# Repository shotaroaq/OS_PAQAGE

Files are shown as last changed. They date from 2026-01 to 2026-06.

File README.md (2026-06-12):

# OS-PAQAGE

"[Open Source microwave Packaging for quantum systems (OS-PAQAGE)](https://doi.org/10.5281/zenodo.18399469)" is a collection of PCB and magnetic-shielded sample-holder designs intended primarily for microwave-frequency use. These designs were developed mainly at RIKEN in Japan and are widely used by Japanese research institutes and universities. Using this package, measurements of superconducting qubits with energy relaxation times exceeding 400 us [1] and observations of internal Q factors above 1e7 in superconducting resonators at the single-photon level have been reported [2].

In fundamental research, there are still many situations where small samples are studied but a clean electromagnetic environment is required. To broaden the available options for building such measurement environments, we decided to release the contents of this repository as open source.

[1] [A. Noguchi, et al. "High-performance transmon qubits with an epitaxially grown TiN film on Si (100) substrate." 2023 APS March Meeting. 2023.](https://meetings.aps.org/Meeting/MAR23/Session/M73.5)
[2] [Y. Tominaga, et al. "Intrinsic quality factors approaching 10 million in superconducting planar resonators enabled by spiral geometry." EPJ Quantum Technology 12.1 (2025): 60.](https://link.springer.com/article/10.1140/epjqt/s40507-025-00367-w)

## Usage
Please place an order for the jigs with a nearby factory. Assembly instructions are provided in *doc/pcb_sample_holder_instructions.pdf*.
In our case, we outsource PCB manufacturing to KANSAI DENSHI INDUSTRIES.

## License
This repository is released under the MIT License. See `LICENSE`.

## Citation
If you use the contents of this repository, please cite the project in the following format:

```
@Misc{osPAQAGE,
  author = {Shirai, Shotaro and Noguchi, Atsushi},
  title = {{OS-PAQAGE}: A open source microwave packaging for quantum systems},
  year = {2025--},
  url = "https://doi.org/10.5281/zenodo.18399470",
  note = {[Online; accessed <today>]}
}
```

## Acknowledgements
This work has been supported by funding from JST Moonshot R&D Program (Grant Number JPMJMS2067)

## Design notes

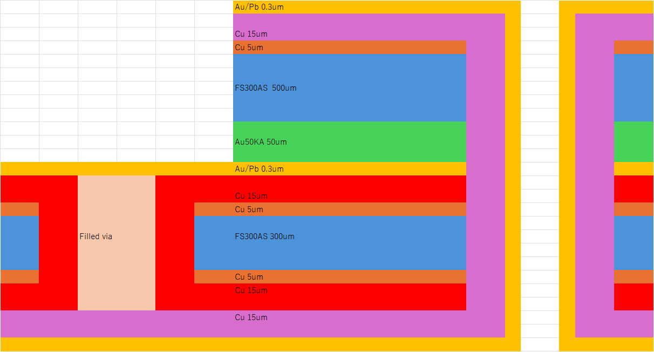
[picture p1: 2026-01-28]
pcb/layer.png

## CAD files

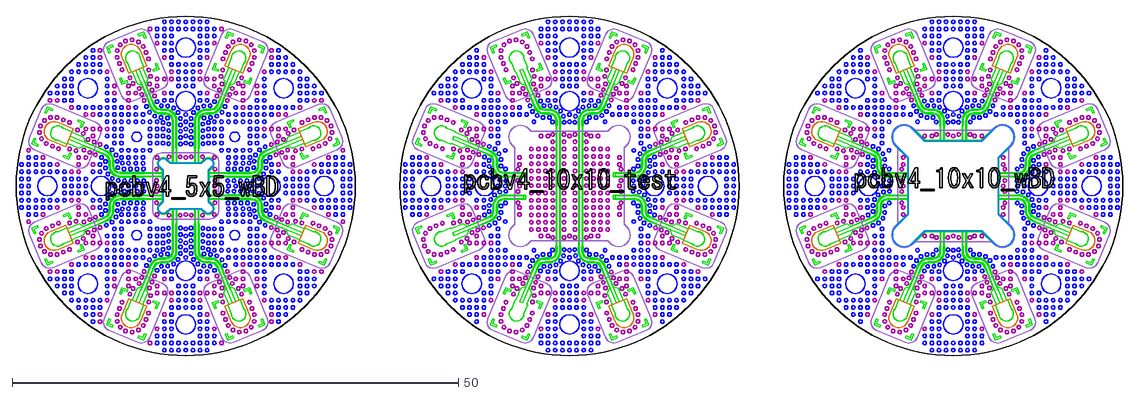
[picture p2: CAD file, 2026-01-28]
pcb/3lay_Cavity_240918.dxf
124.0 x 38.0

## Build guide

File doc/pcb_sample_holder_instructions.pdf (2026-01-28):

# Small scale sample holder and PCB

## RIKEN Center for Quantum Computing Komaba Institute for Science, UTokyo

## Shotaro Shirai, Atsushi Noguchi

Ver0.1 2024/10/09

Ver0.2 2024/10/13

Ver0.3 2024/11/07

Ver0.4 2025/04/08

Ver0.5 2025/06/10

Ver0.6 2026/01/26

# Sample holder design

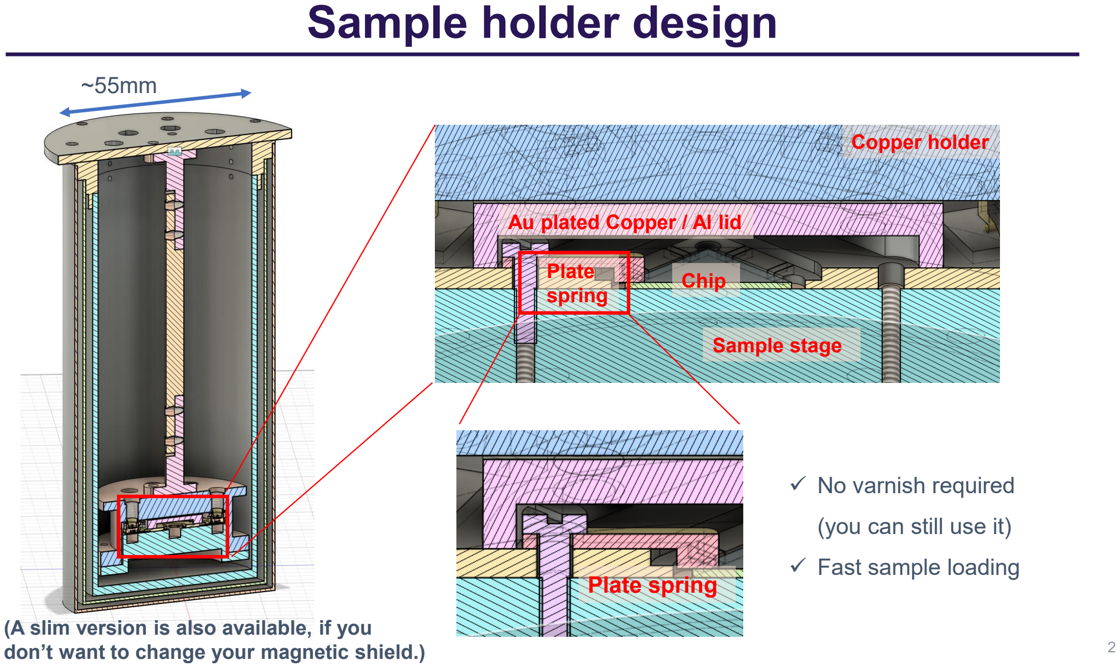
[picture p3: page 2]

~55mm

Au plated Copper / Al lid

Copper holder

Sample stage

Chip Plate
spring

Plate spring

✓ No varnish required

(you can still use it)

✓ Fast sample loading

(A slim version is also available, if you don’t want to change your magnetic shield.)

# PCB design

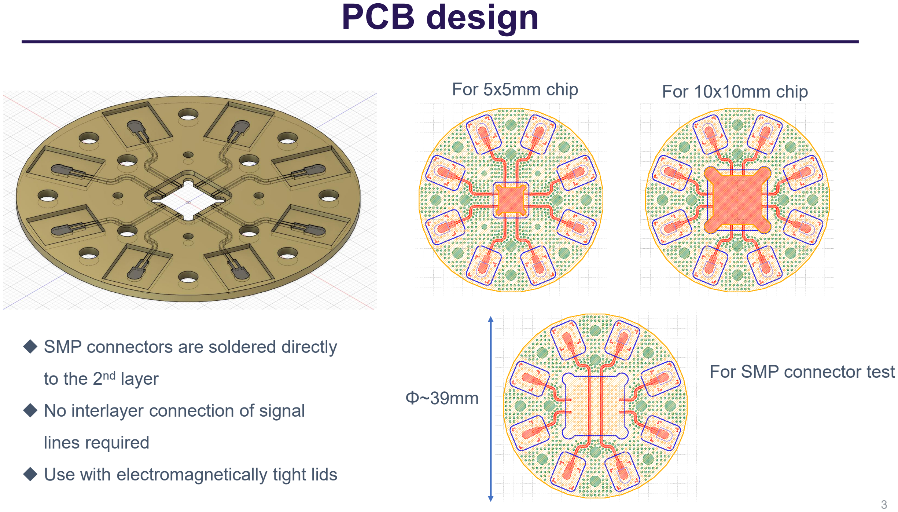
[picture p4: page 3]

For 5x5mm chip | For 10x10mm chip

For SMP connector test

◆ SMP connectors are soldered directly

to the 2nd layer

◆ No interlayer connection of signal

lines required

◆ Use with electromagnetically tight lids

Φ~39mm

# Assembling PCB

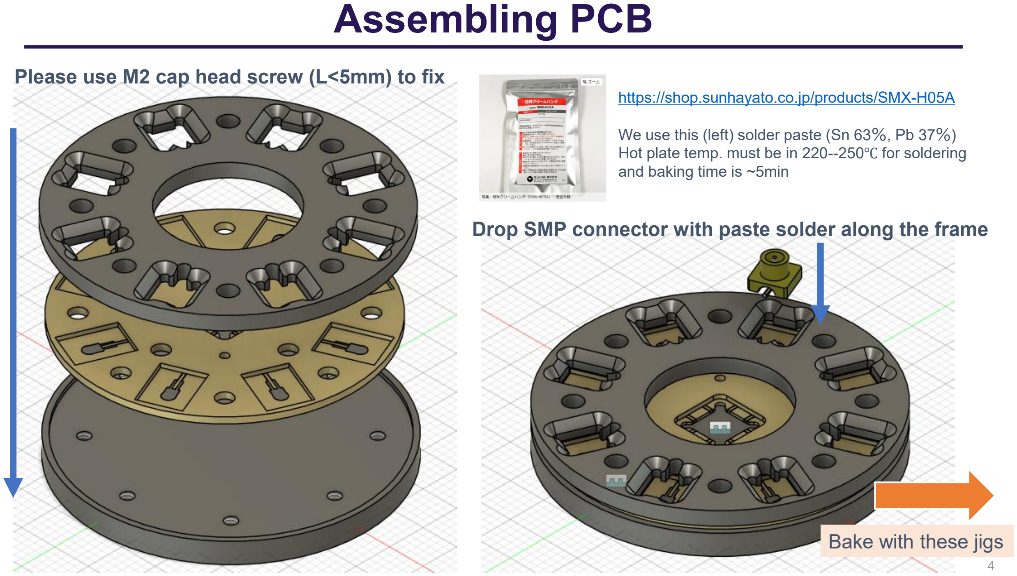
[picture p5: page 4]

Please use M2 cap head screw (L<5mm) to fix

Drop SMP connector with paste solder along the frame https://shop.sunhayato.co.jp/products/SMX-H05A

We use this (left) solder paste (Sn 63％, Pb 37％) Hot plate temp. must be in 220--250℃ for soldering and baking time is ~5min

Bake with these jigs

# Assembling PCB: cable and connectors

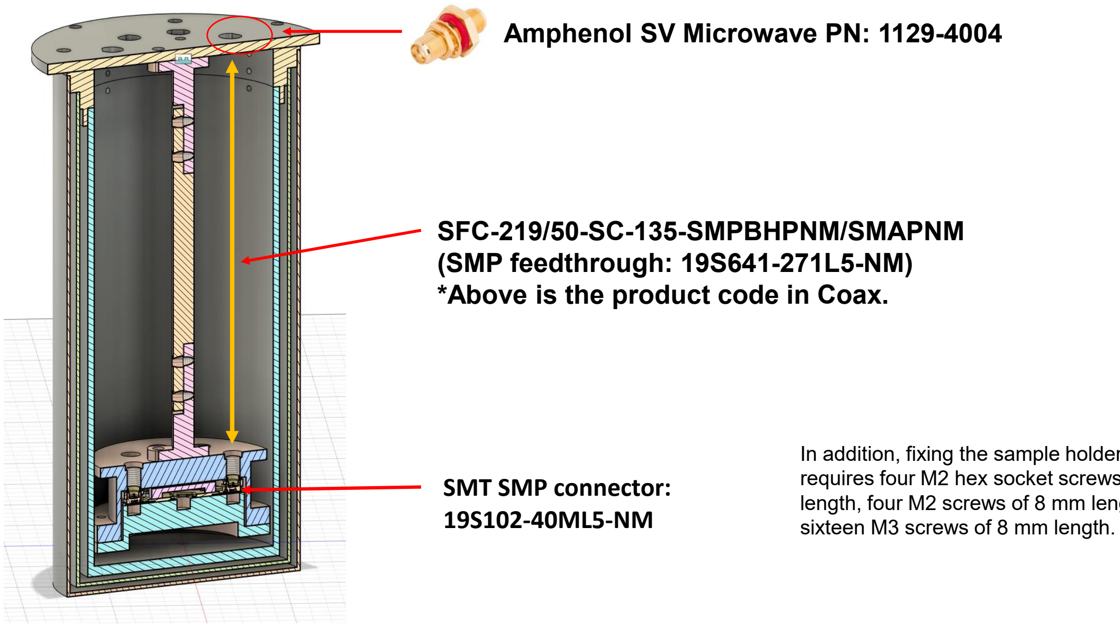
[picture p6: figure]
SMT SMP connector: 19S102-40ML5-NM; SFC-219/50-SC-135-SMPBHPNM/SMAPNM (SMP feedthrough: 19S641-271L5-NM) *Above is the product code in Coax.; Amphenol SV Microwave PN: 1129-4004; sixteen M3 screws of 8 mm length.

In addition, fixing the sample holder and lid requires four M2 hex socket screws of 5 mm length, four M2 screws of 8 mm length, and

# Chip assembling

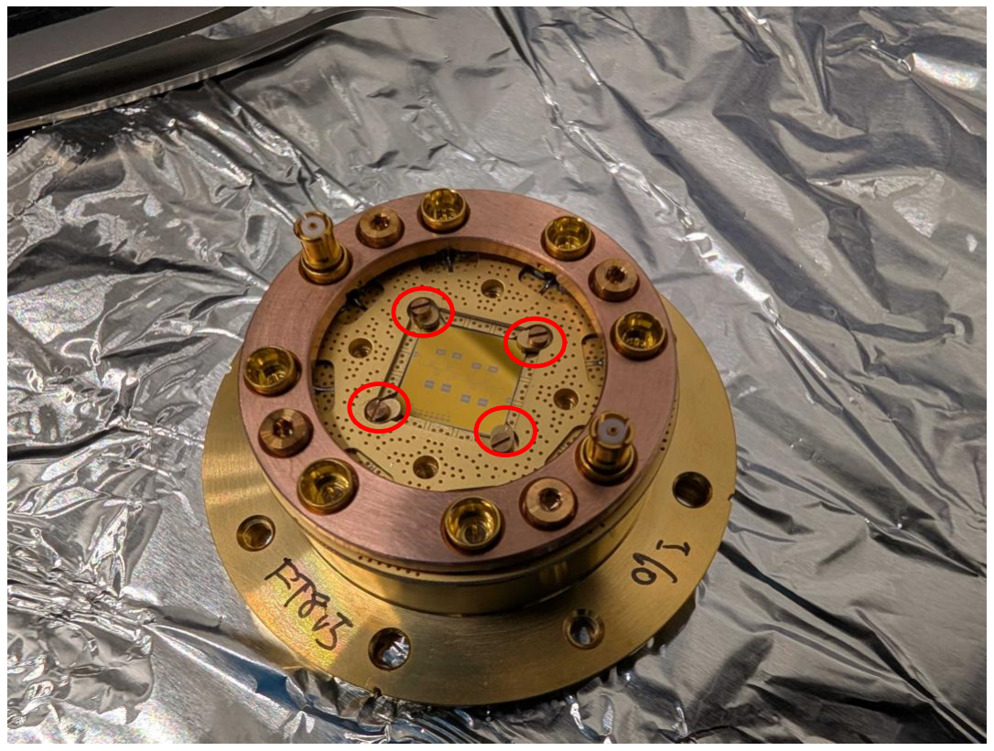
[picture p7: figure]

The chip can be fixed either by using varnish or mechanically, as shown in the photo, by fastening a fixture with M1 screws (4 mm long). We recommend fixing with varnish.

# SMP connector’s reflection and PCB loss

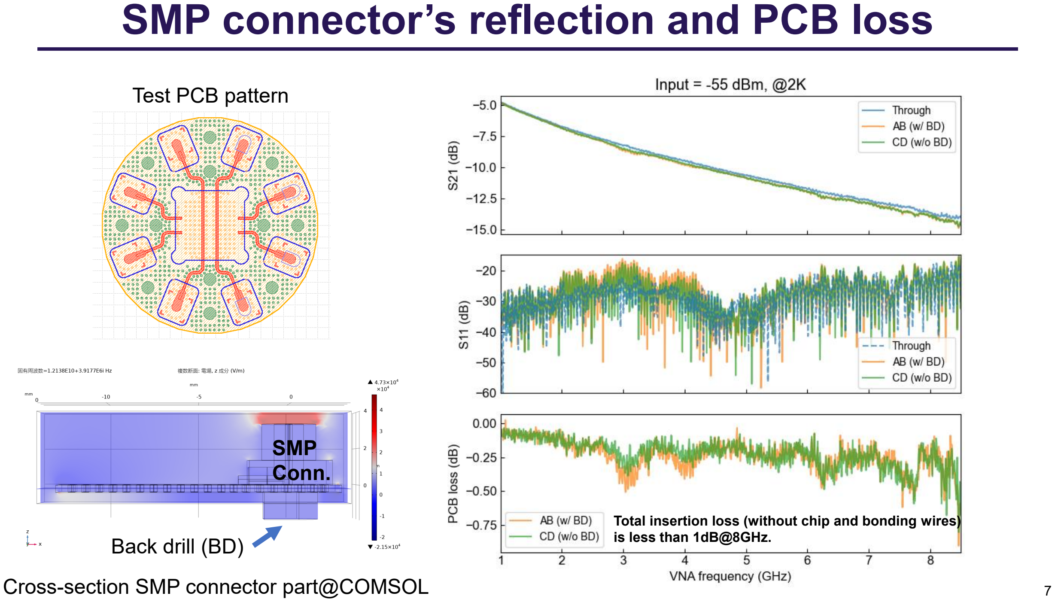
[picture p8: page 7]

Test PCB pattern

Total insertion loss (without chip and bonding wires) is less than 1dB@8GHz.

Cross-section SMP connector part@COMSOL

Back drill (BD)

SMP
Conn.

# SMP connector’s reflection and PCB loss

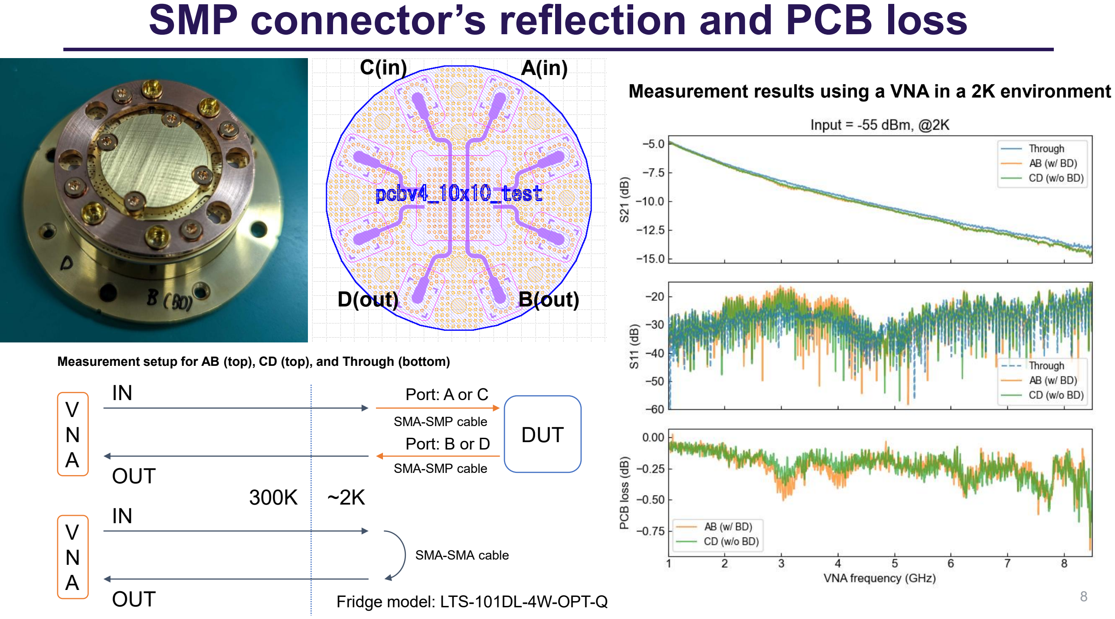
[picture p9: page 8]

A(in)

B(out)

C(in)

D(out)

Measurement results using a VNA in a 2K environment

V
N
A

DUT

IN

OUT
300K ~2K

Port: A or C

Port: B or D

SMA-SMP cable

SMA-SMP cable

V
N
A

IN

OUT

SMA-SMA cable

Measurement setup for AB (top), CD (top), and Through (bottom)

Fridge model: LTS-101DL-4W-OPT-Q

# PCB loss including a chip and bonding wires

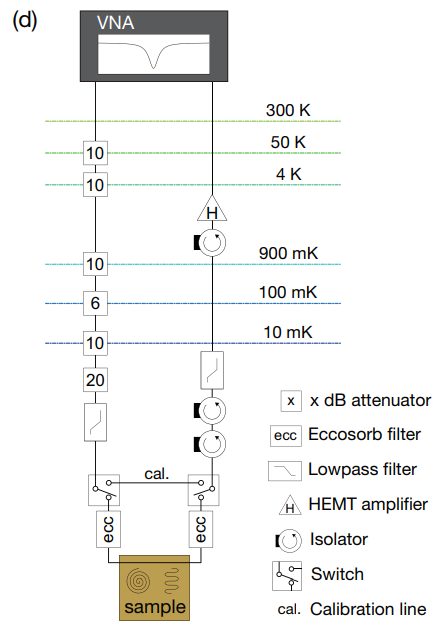
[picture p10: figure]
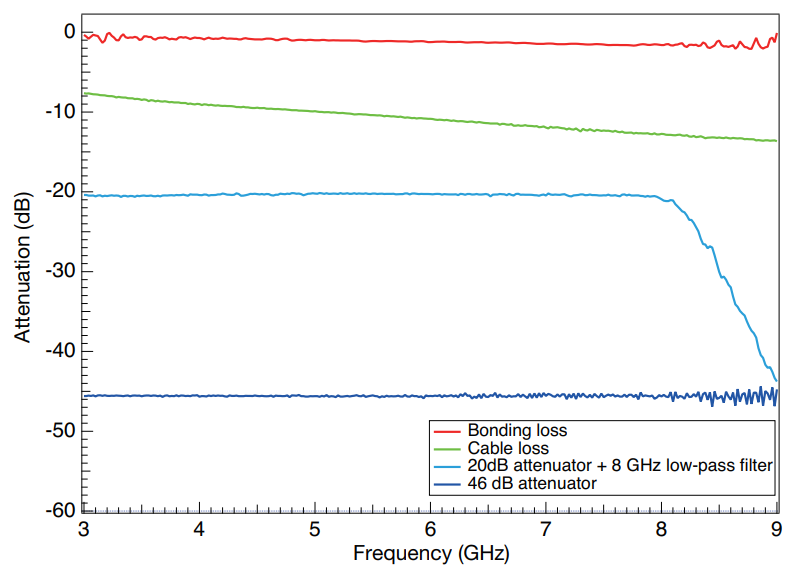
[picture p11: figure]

[1] Y. Tominaga, et al., "Intrinsic quality factors approaching 10 million in superconducting planar resonators enabled by spiral geometry." EPJ Quantum Technology 12.1 (2025).

The total loss of the SMP connectors, PCB, bonding wires, and a chip after calibration in the 10 mK environment is approximately 1 dB, and when following the appropriate sample loading procedure (described below), no significant resonant structures have been observed in the 3–8 GHz range.

Using this PCB and sample holder, internal Q-factors exceeding 10⁷ at the single-photon level have been observed for microwave resonators, and in the high-power regime, the internal Q-factor approaches 10⁸. For these results and detailed calibration procedures, please refer to Ref. [1].

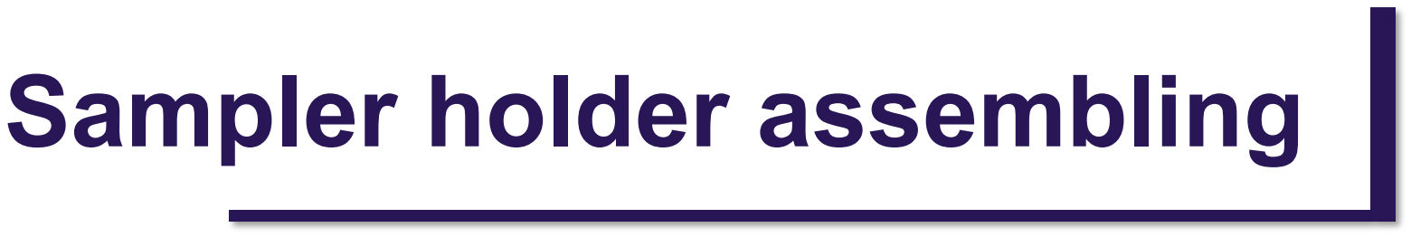
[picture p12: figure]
Sampler holder assembling

# Note

- One known issue at present, as explained below, is crosstalk between SMP connectors mediated by modes in the space between the central lid of the sample holder and the surrounding copper ring.
This can be mitigated by grounding unused ports or sealing the gap with metallic tape. In the future, this issue can be addressed by designing a more tightly fitting lid.

# Assembled sample stage and PCB

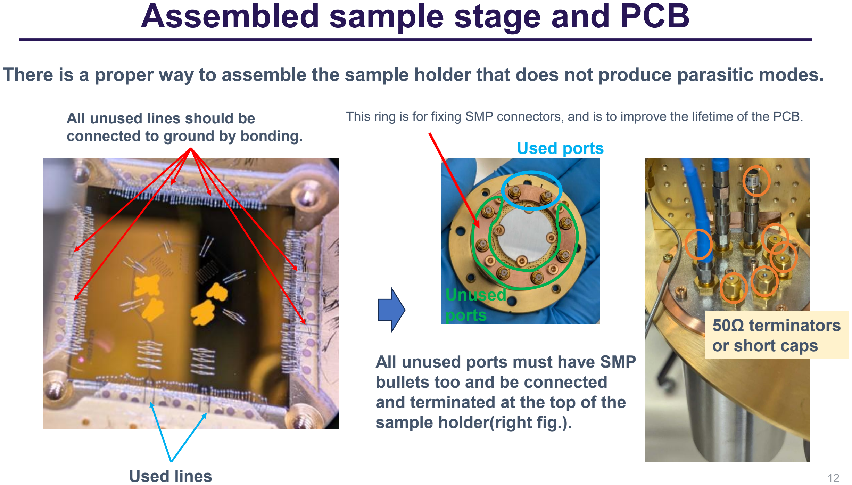
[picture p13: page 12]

There is a proper way to assemble the sample holder that does not produce parasitic modes.

Used lines

All unused lines should be connected to ground by bonding.

All unused ports must have SMP bullets too and be connected and terminated at the top of the sample holder(right fig.).

Used ports

50Ω terminators
or short caps

This ring is for fixing SMP connectors, and is to improve the lifetime of the PCB.

Unused
ports

# S21 measurement @ Room temperature

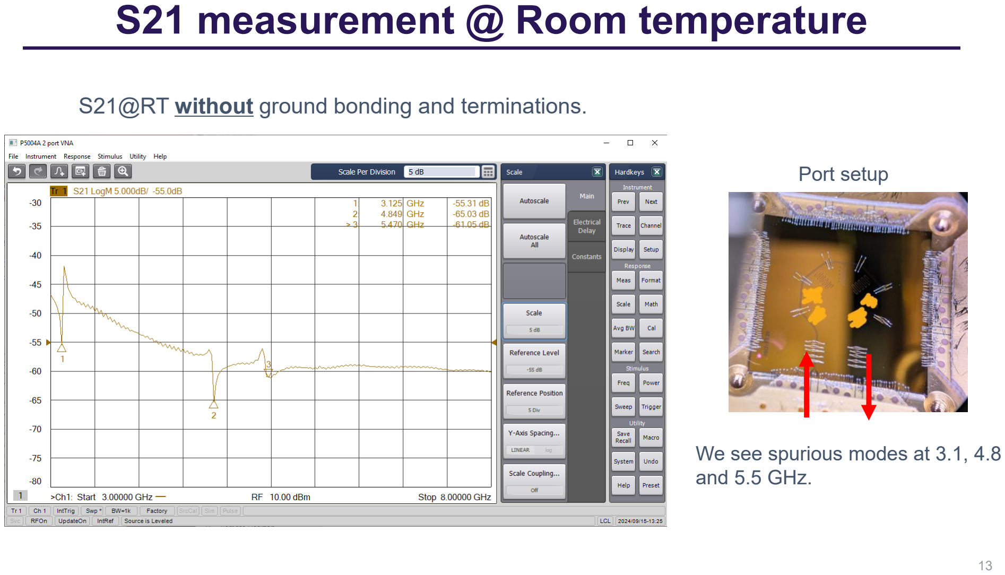
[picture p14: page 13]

S21@RT without ground bonding and terminations.

We see spurious modes at 3.1, 4.8 and 5.5 GHz.

Port setup

# S21 measurement (Crosstalk) @ Room temperature

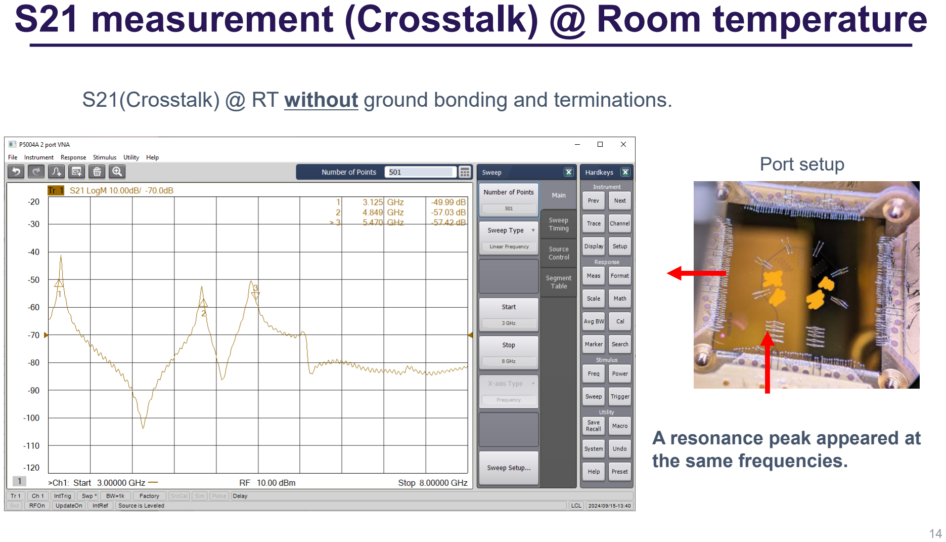
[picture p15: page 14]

S21(Crosstalk) @ RT without ground bonding and terminations.

A resonance peak appeared at the same frequencies.

Port setup

# S21 measurement (Crosstalk) @ Room temperature

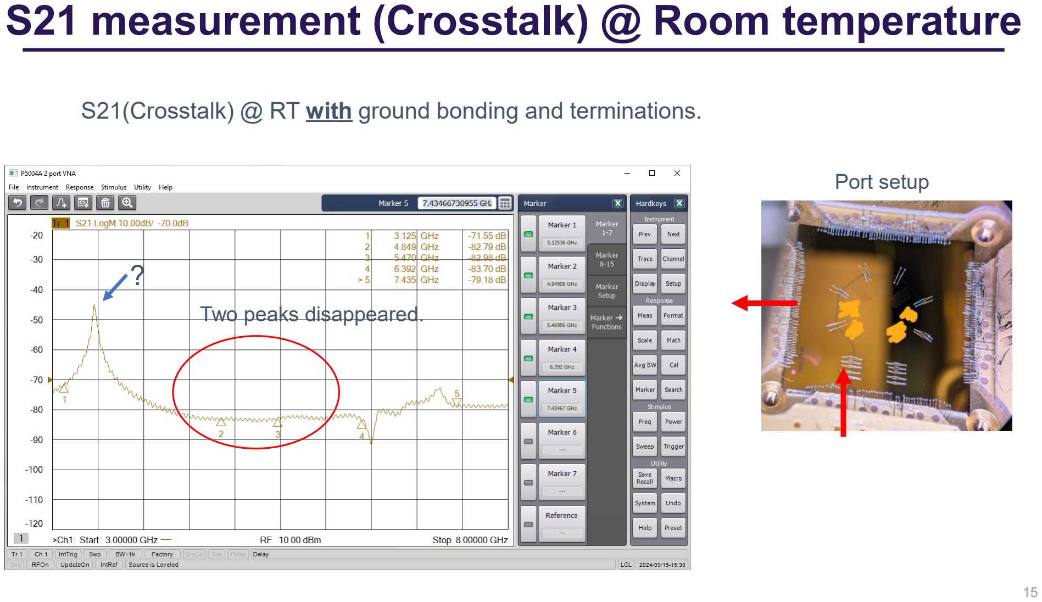
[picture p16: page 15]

S21(Crosstalk) @ RT with ground bonding and terminations.

Port setup

Two peaks disappeared.

?

# RT S21 measurement (Crosstalk)

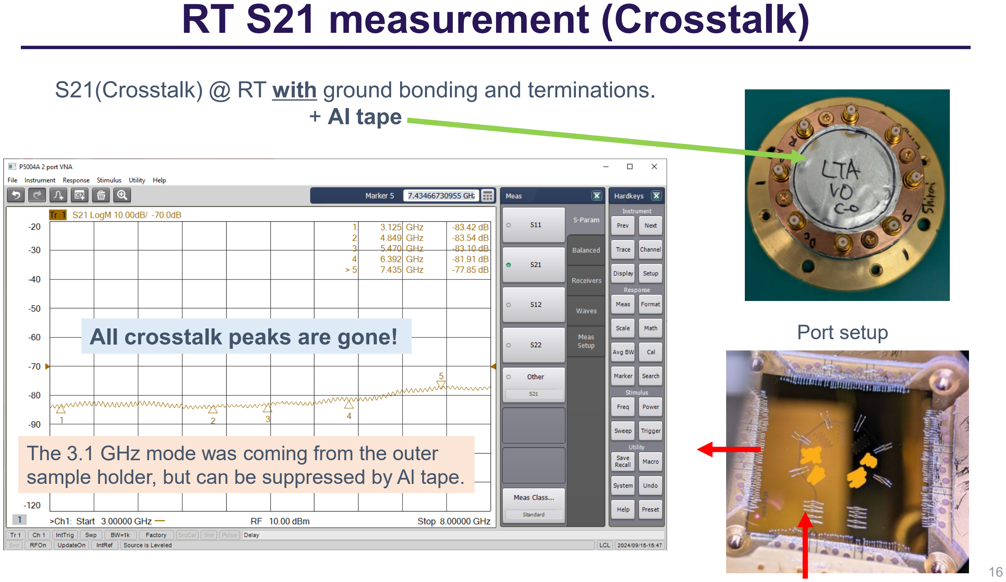
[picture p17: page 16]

S21(Crosstalk) @ RT with ground bonding and terminations. + Al tape

Port setup

Two peaks disappeared.

?

All crosstalk peaks are gone!

The 3.1 GHz mode was coming from the outer sample holder, but can be suppressed by Al tape.

# PCB layer

Au/Pb 0.3um

Cu 15um
Cu 5um

FS300AS 500um

Au50KA 50um

Au/Pb 0.3um

Cu 15um
Cu 5um
Filled via | FS300AS 300um

Cu 5um
Cu 15um

Cu 15um

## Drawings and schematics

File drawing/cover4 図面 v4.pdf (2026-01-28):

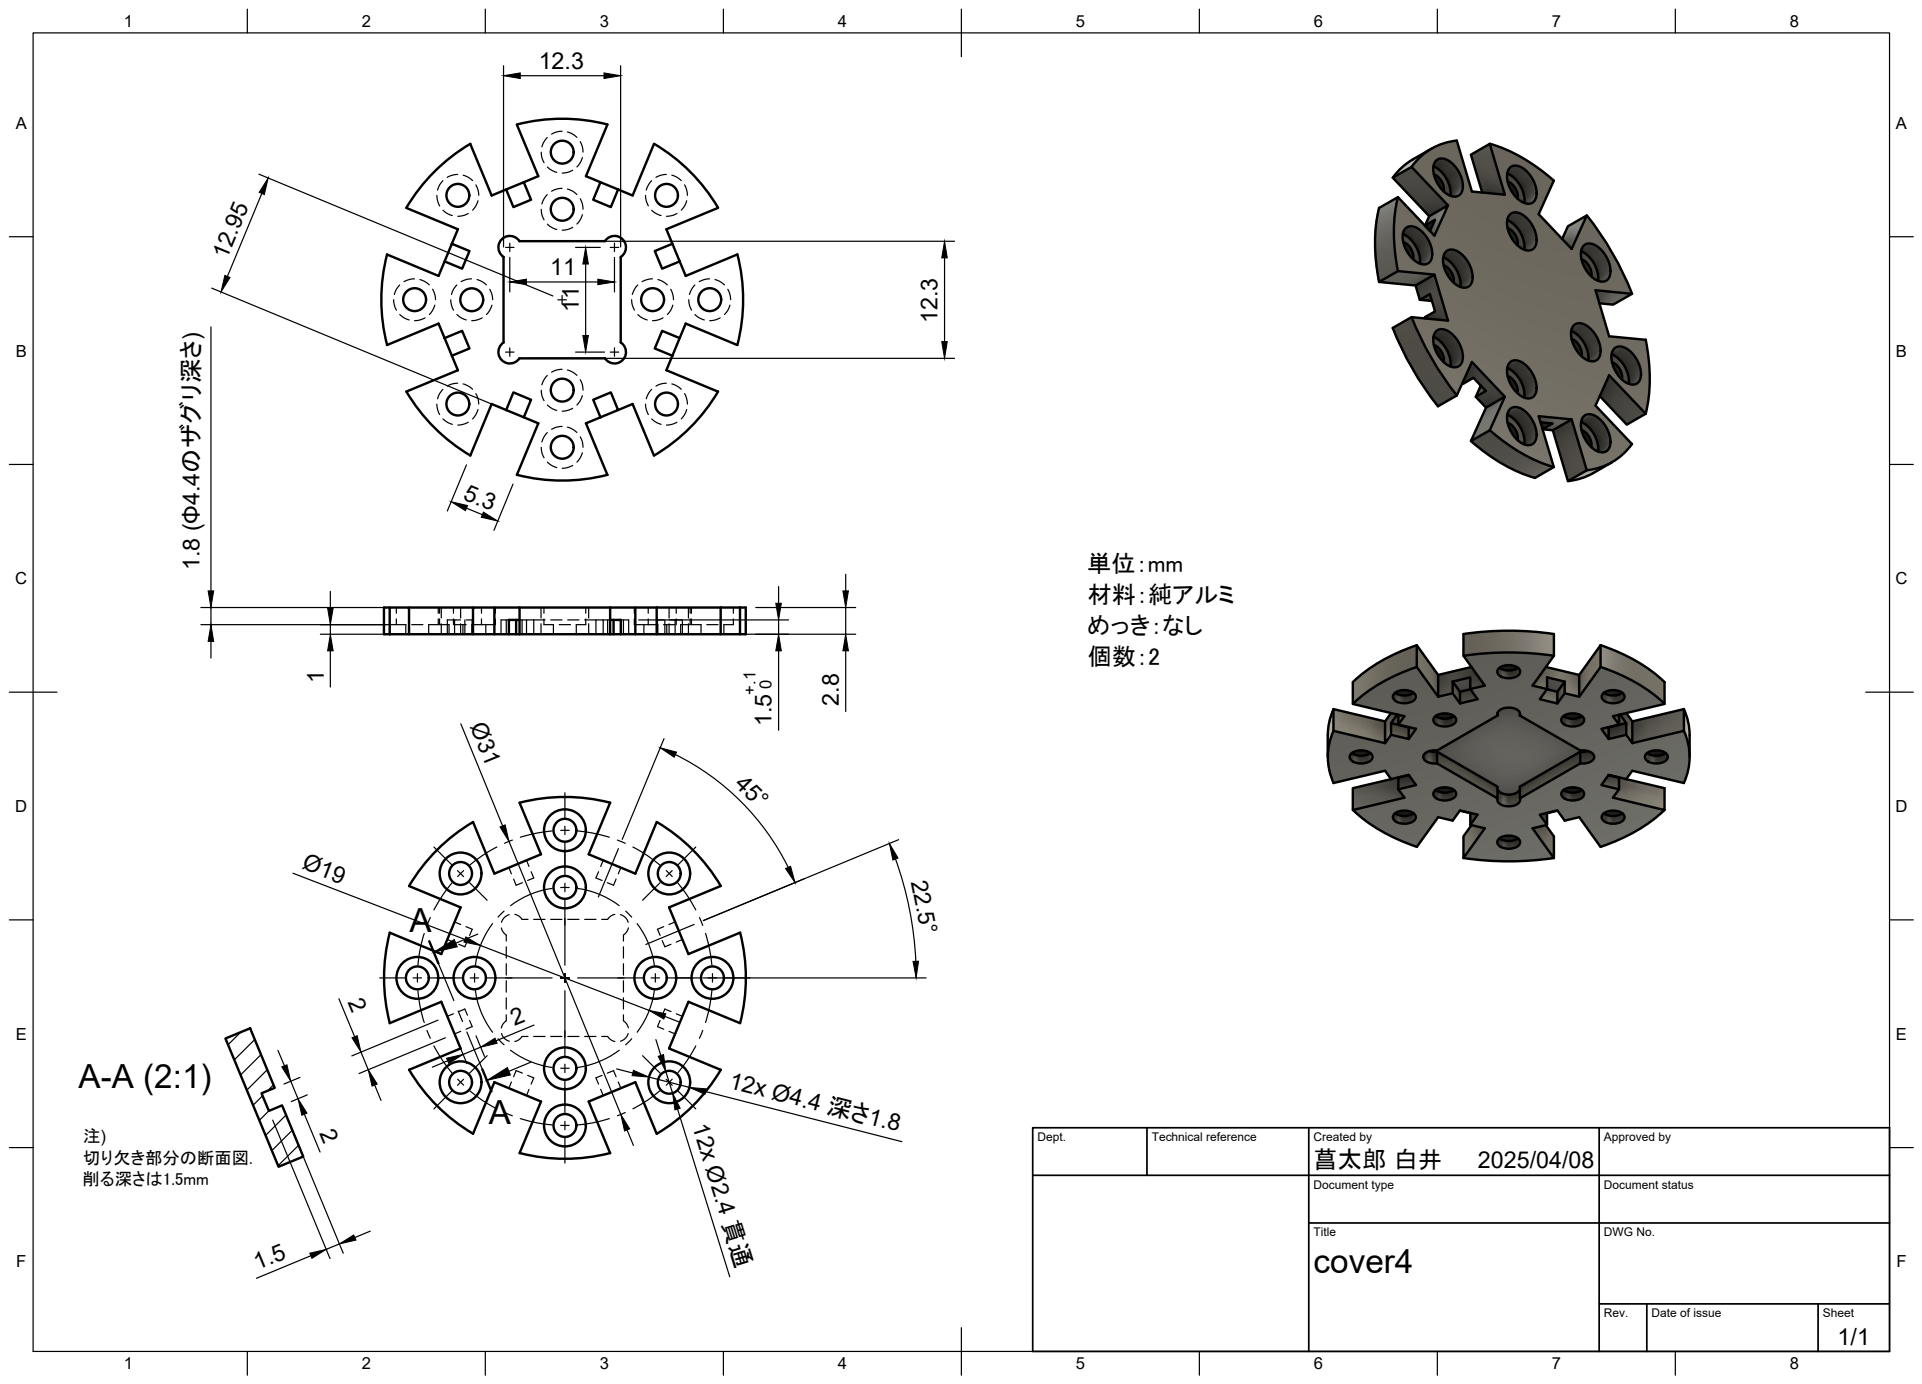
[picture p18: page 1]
8 BCDEF; ABCDEF; Title; DWG No.; Rev.; Date of issue; Sheet; 菖太郎 白井 2.8 1.5+.1 01 1.8 (Φ4.4のザグリ深さ); 削る深さは1.5mm

Dept. | Technical reference | Created by 2025/04/08 | Approved by

Document type | Document status

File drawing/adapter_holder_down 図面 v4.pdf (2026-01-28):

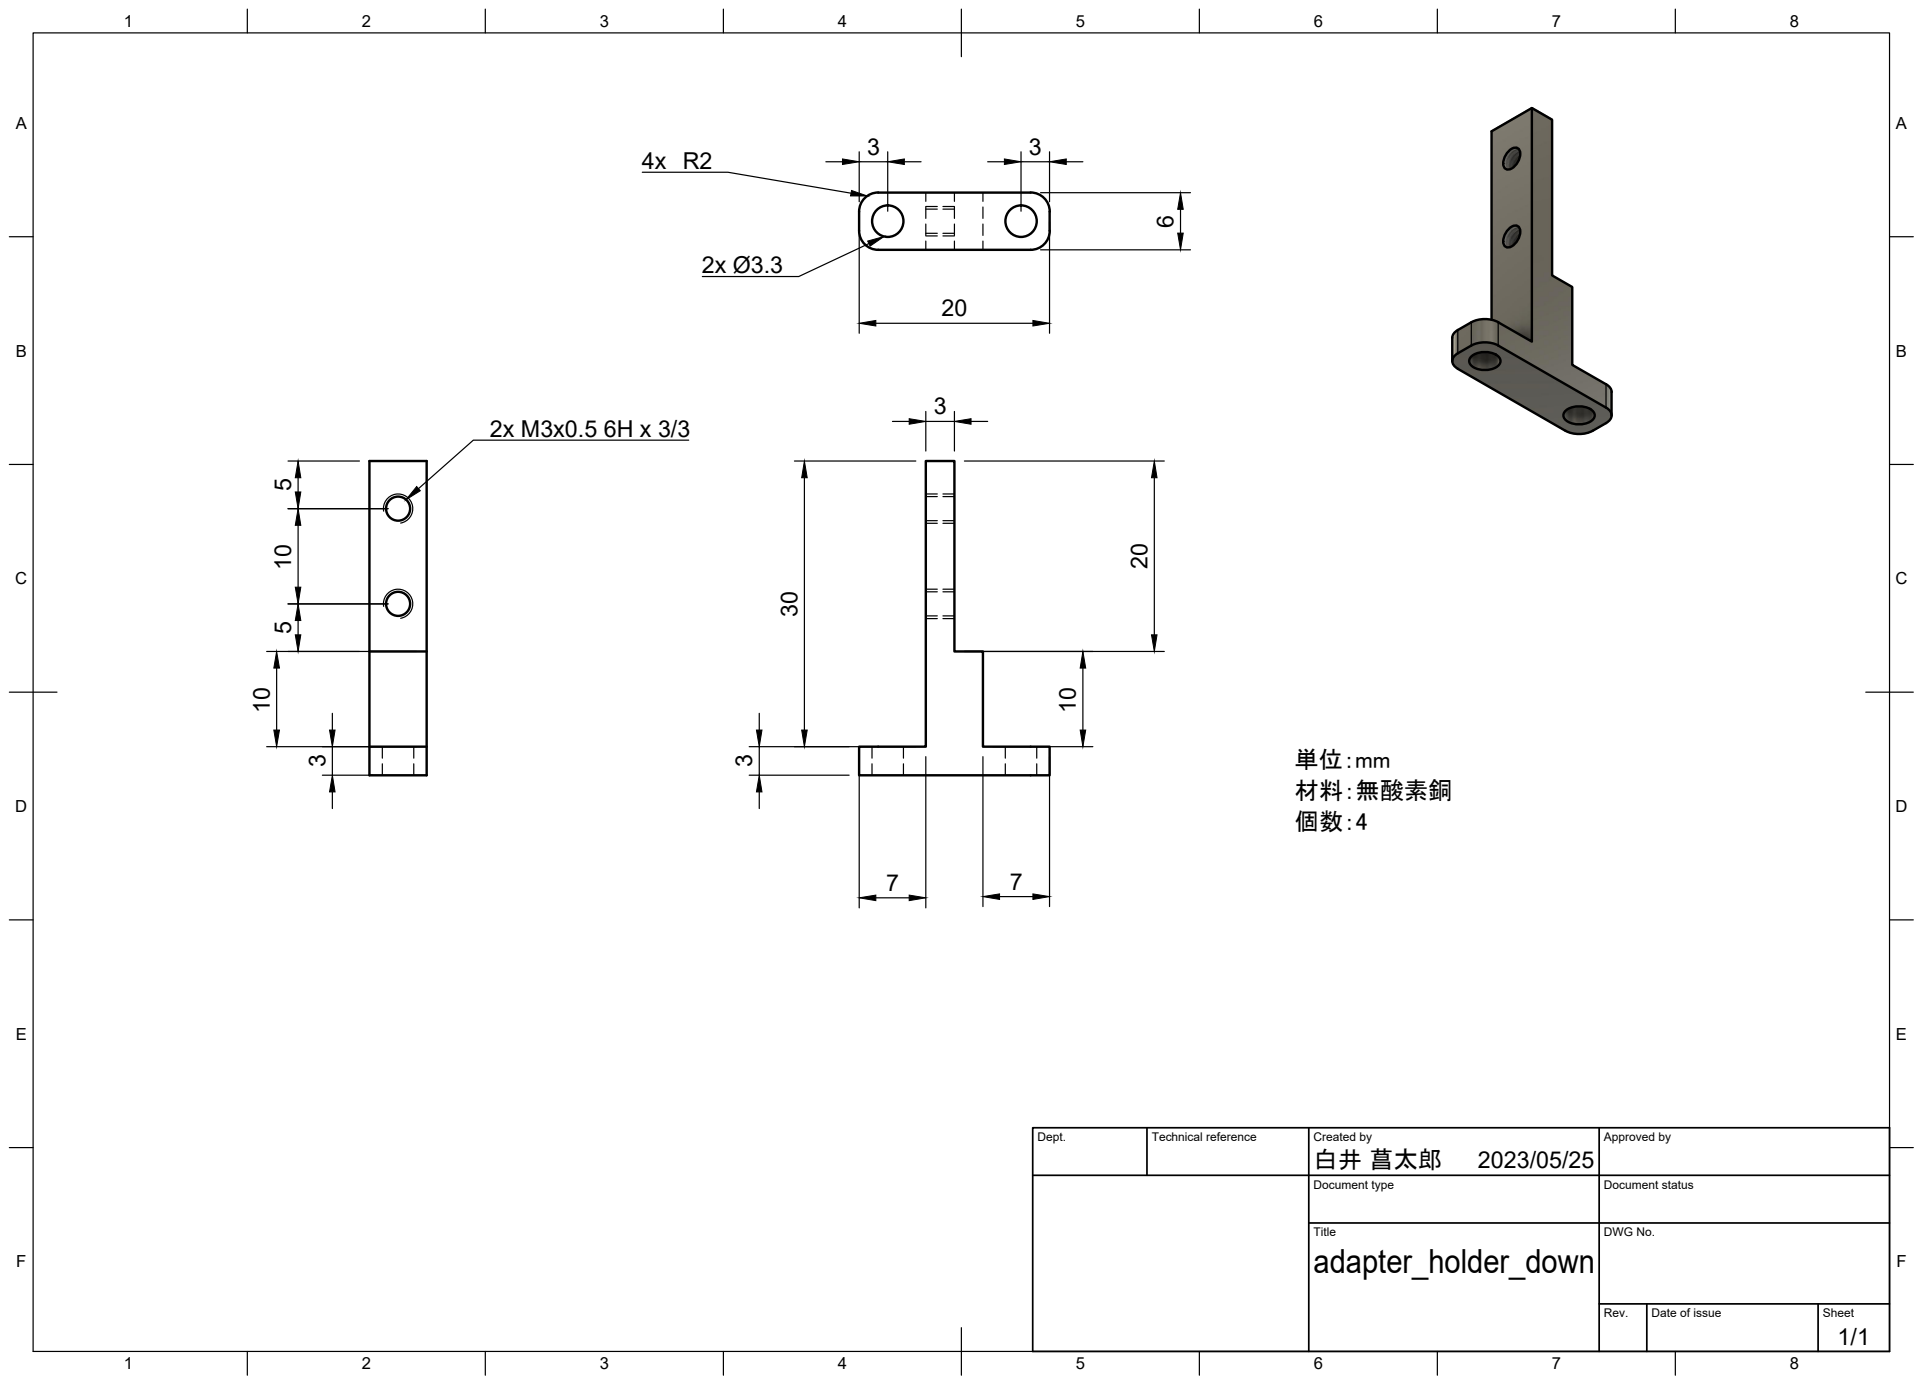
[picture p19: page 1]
Title; DWG No.; Rev.; Date of issue; Sheet

Dept. | Technical reference | Created by 白井 菖太郎 2023/05/25 | Approved by

Document type | Document status

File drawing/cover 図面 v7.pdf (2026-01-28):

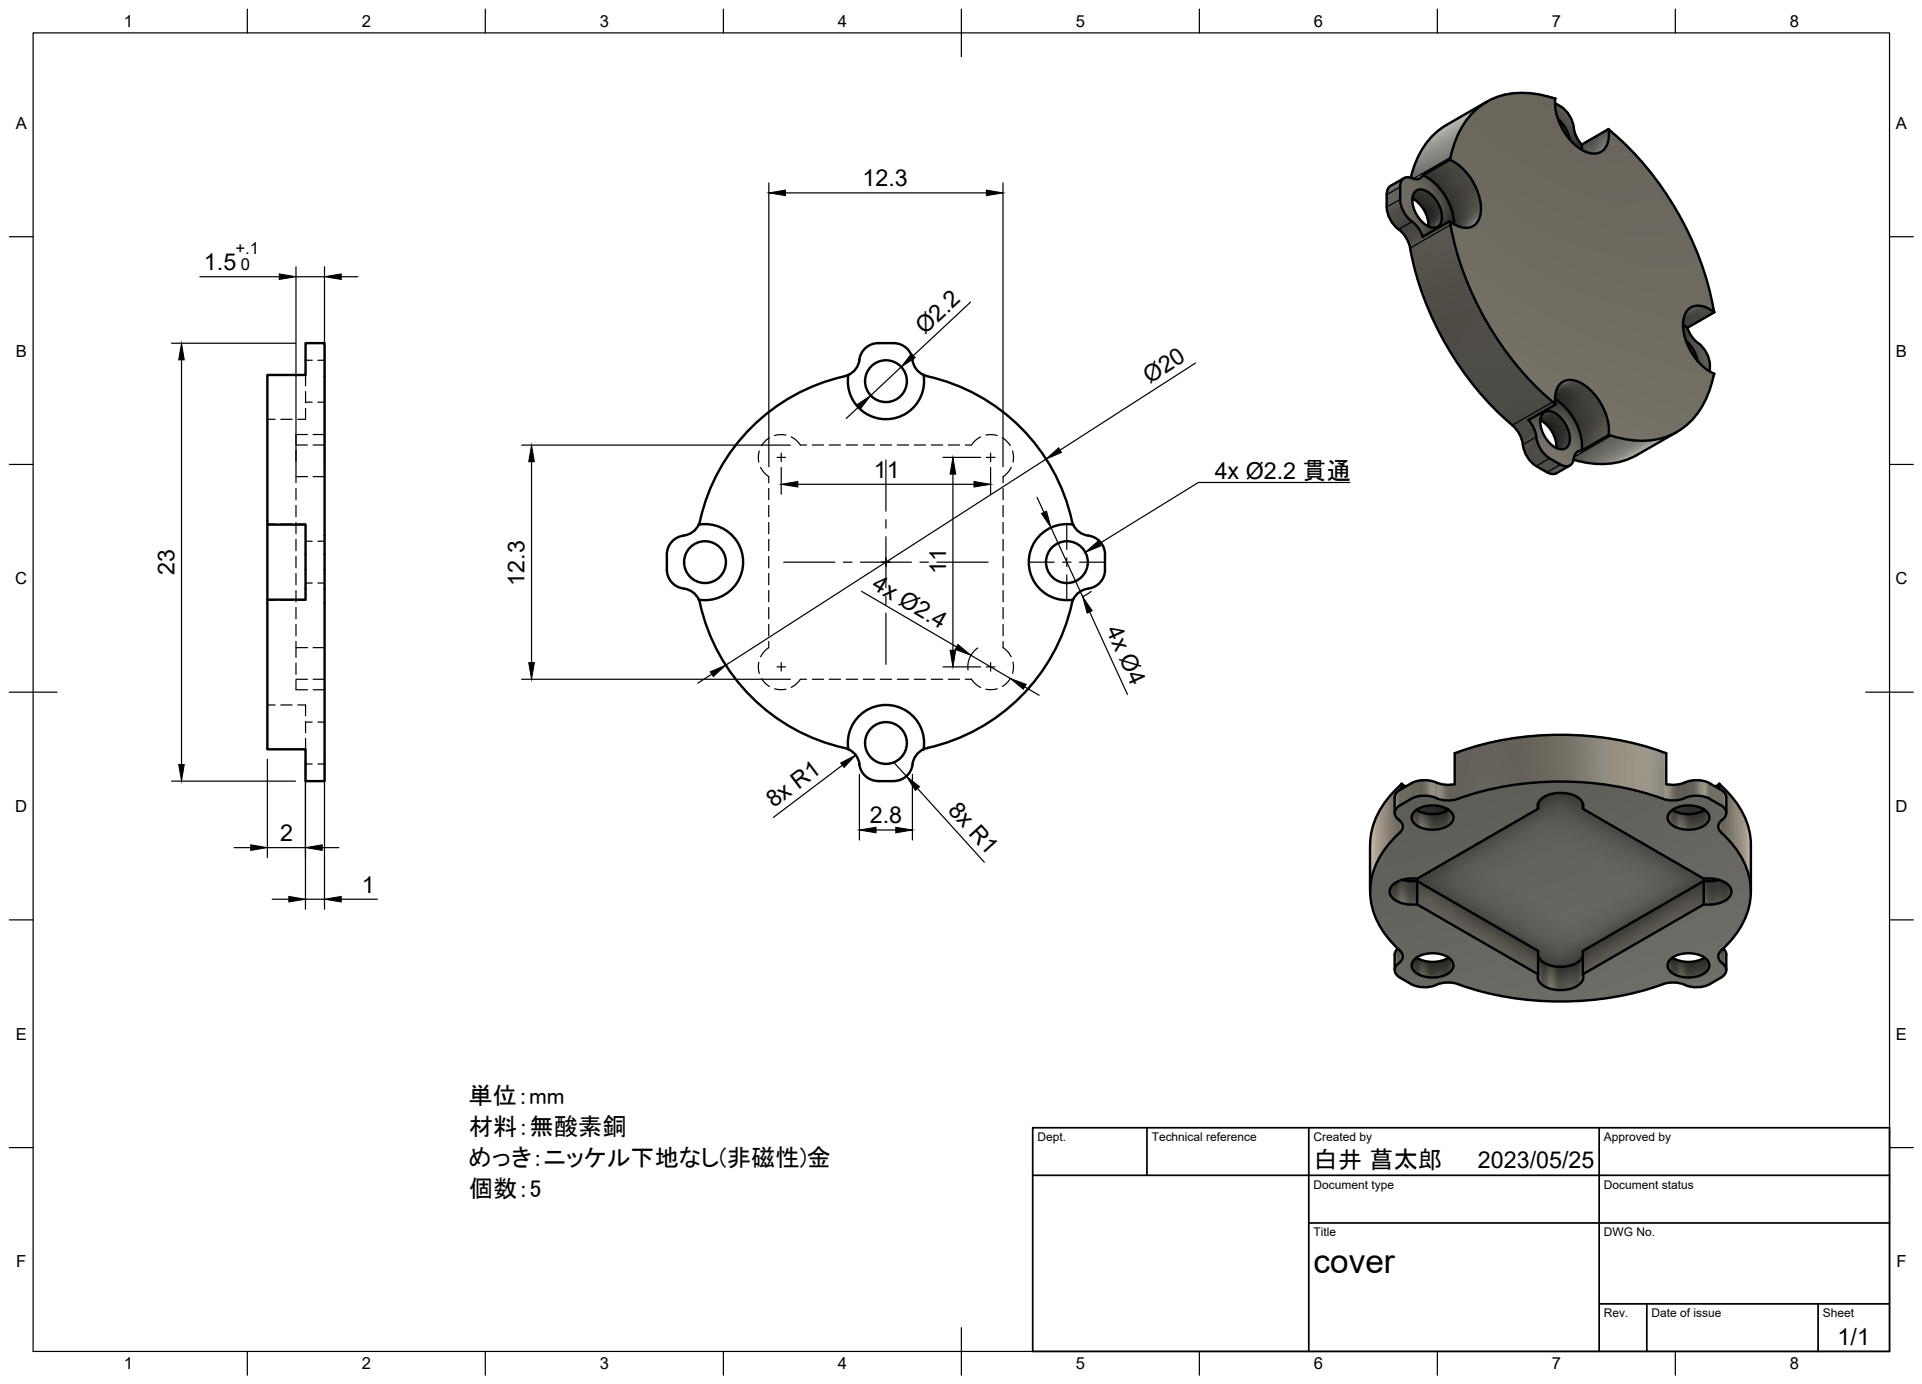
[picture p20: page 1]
Title; DWG No.; Rev.; Date of issue; Sheet

材料：無酸素銅
めっき：ニッケル下地なし(非磁性)金

Dept. | Technical reference | Created by 白井 菖太郎 2023/05/25 | Approved by

Document type | Document status

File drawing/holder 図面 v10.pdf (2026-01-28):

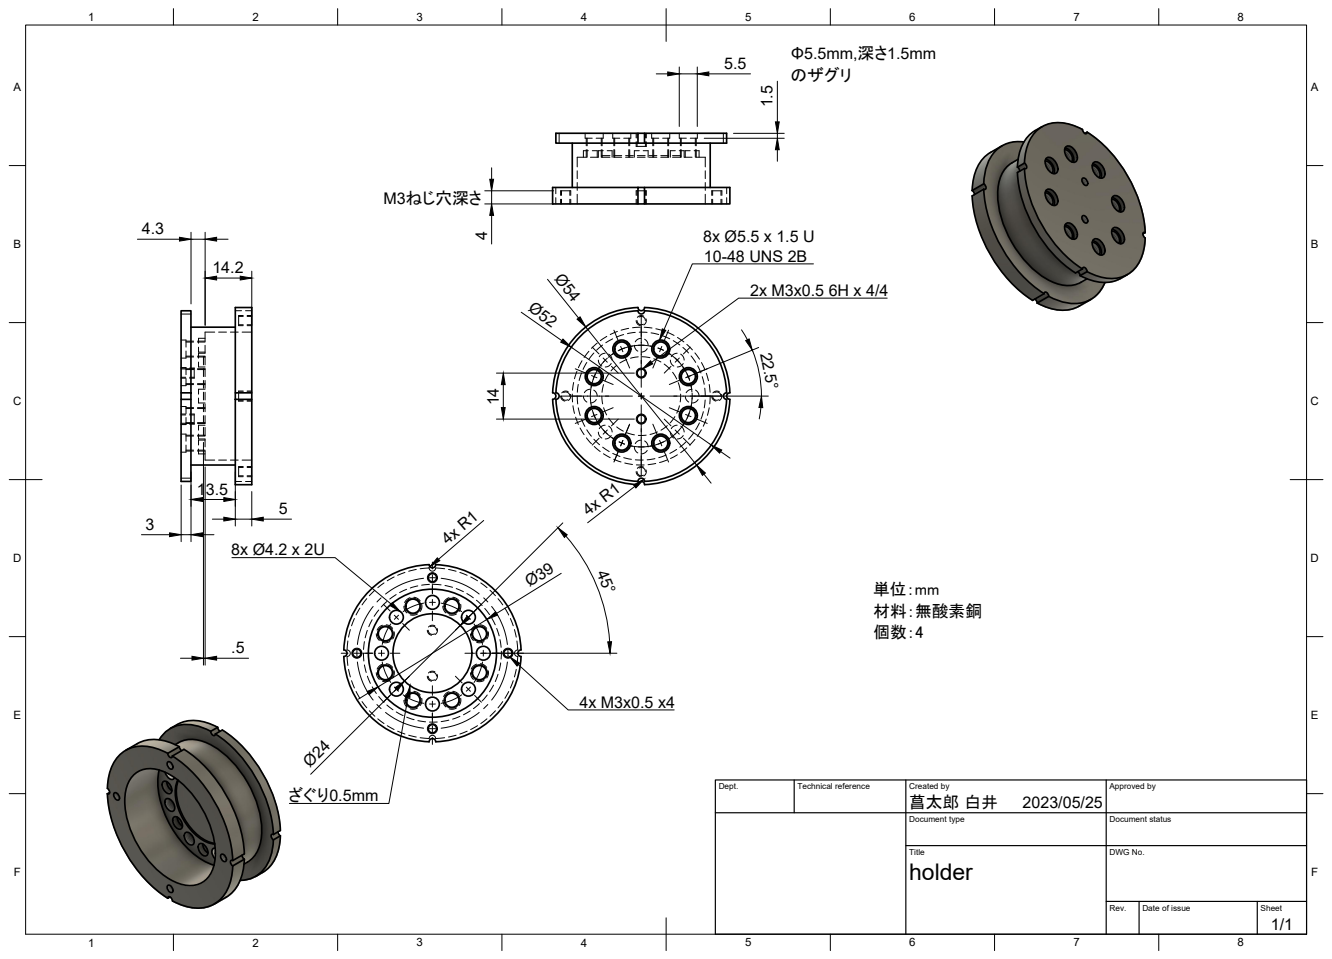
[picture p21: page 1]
Title; DWG No.; Rev.; Date of issue; Sheet; 10-48 UNS 2B 1.5

Dept. | Technical reference | Created by 菖太郎 白井 2023/05/25 | Approved by

Document type | Document status

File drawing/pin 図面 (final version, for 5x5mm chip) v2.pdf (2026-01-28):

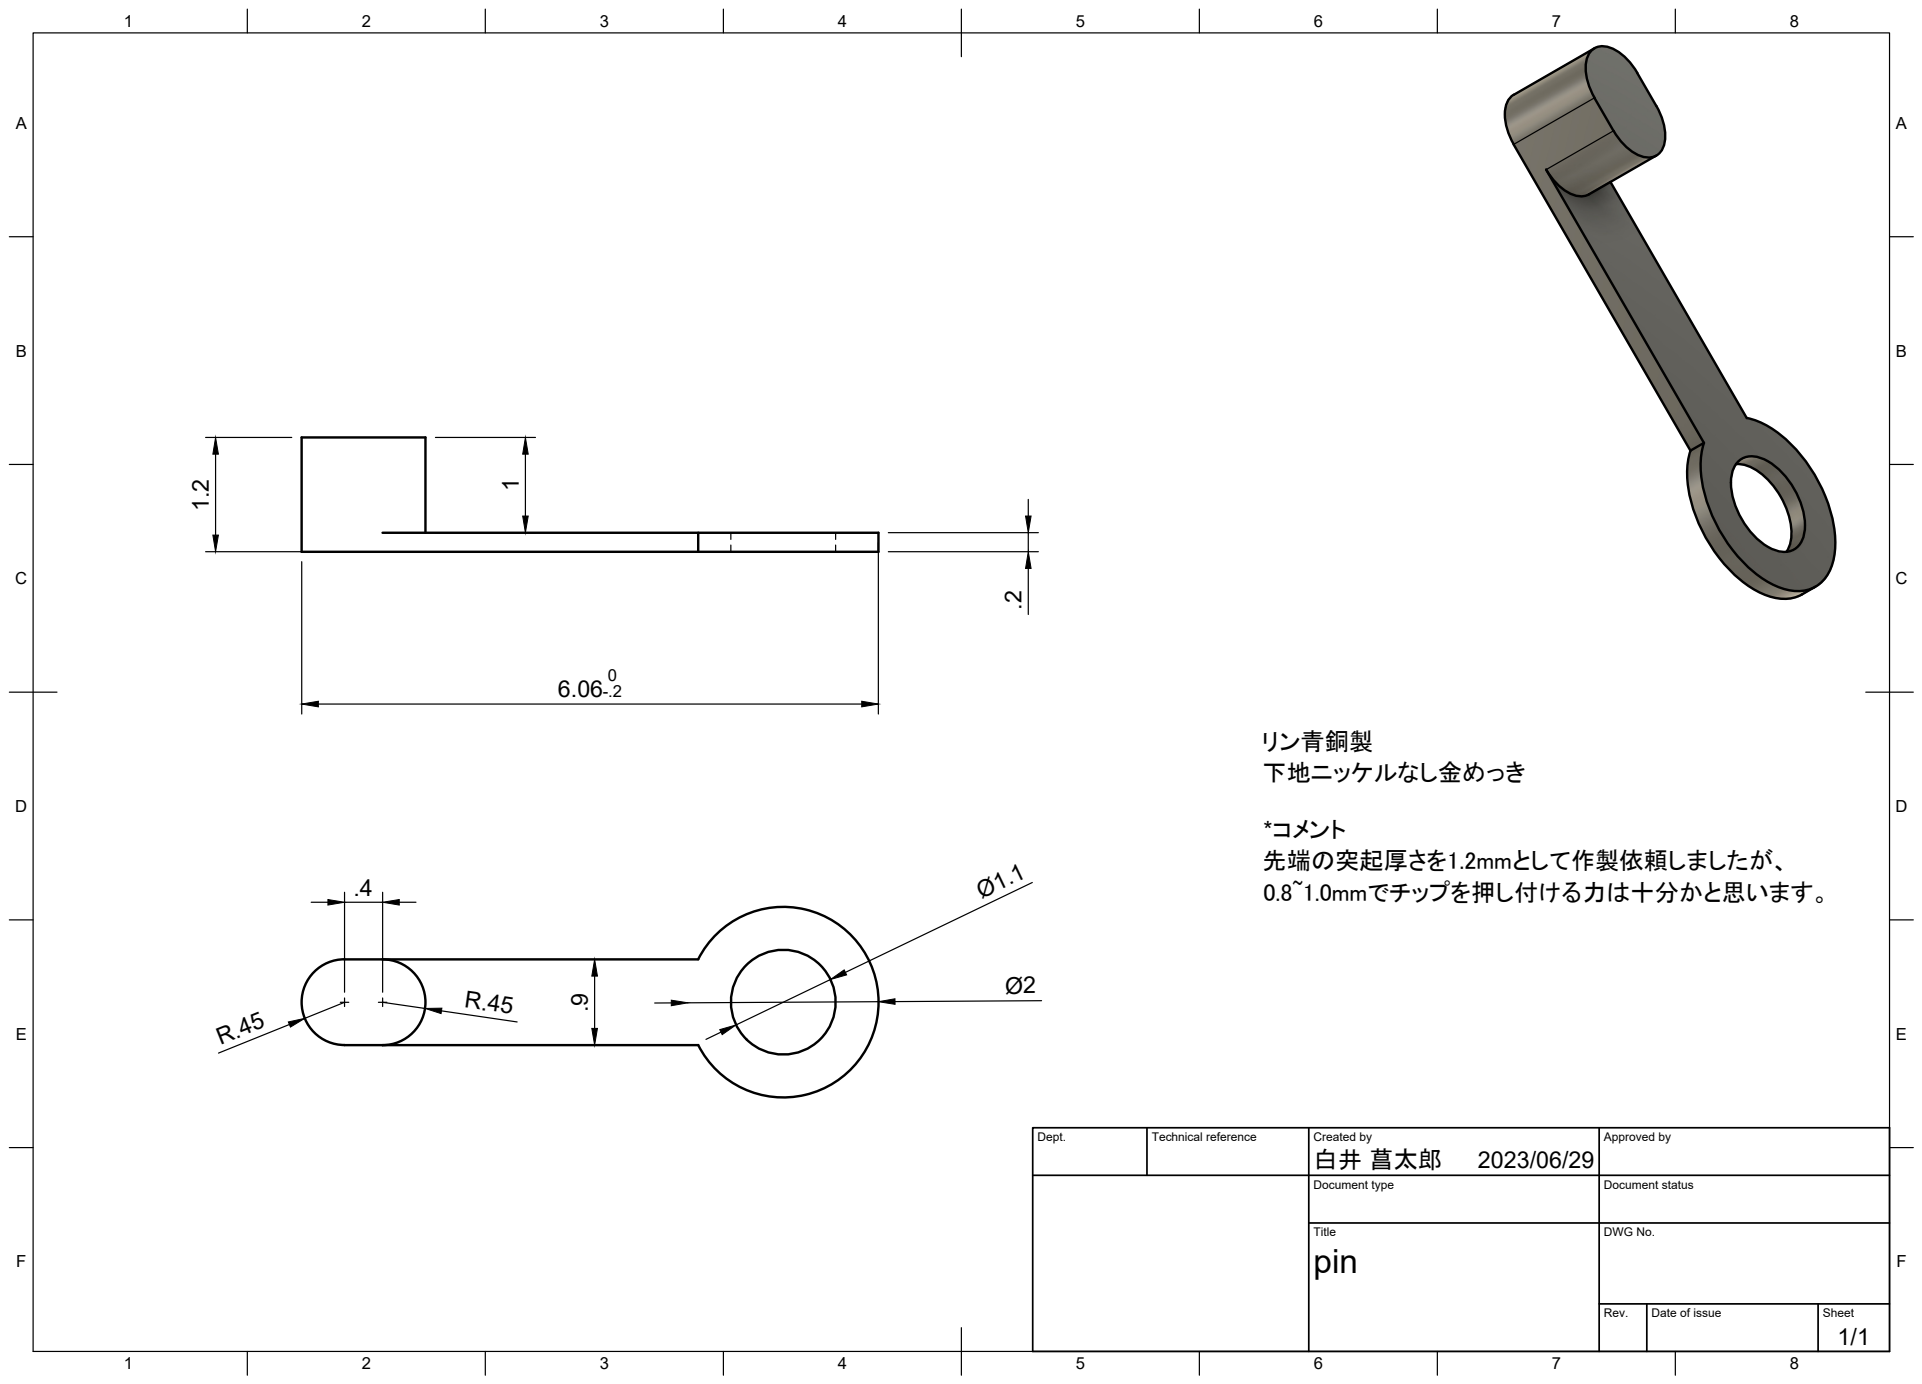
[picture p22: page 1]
Title; DWG No.; Rev.; Date of issue; Sheet

Dept. | Technical reference | Created by 白井 菖太郎 2023/06/29 | Approved by

Document type | Document status

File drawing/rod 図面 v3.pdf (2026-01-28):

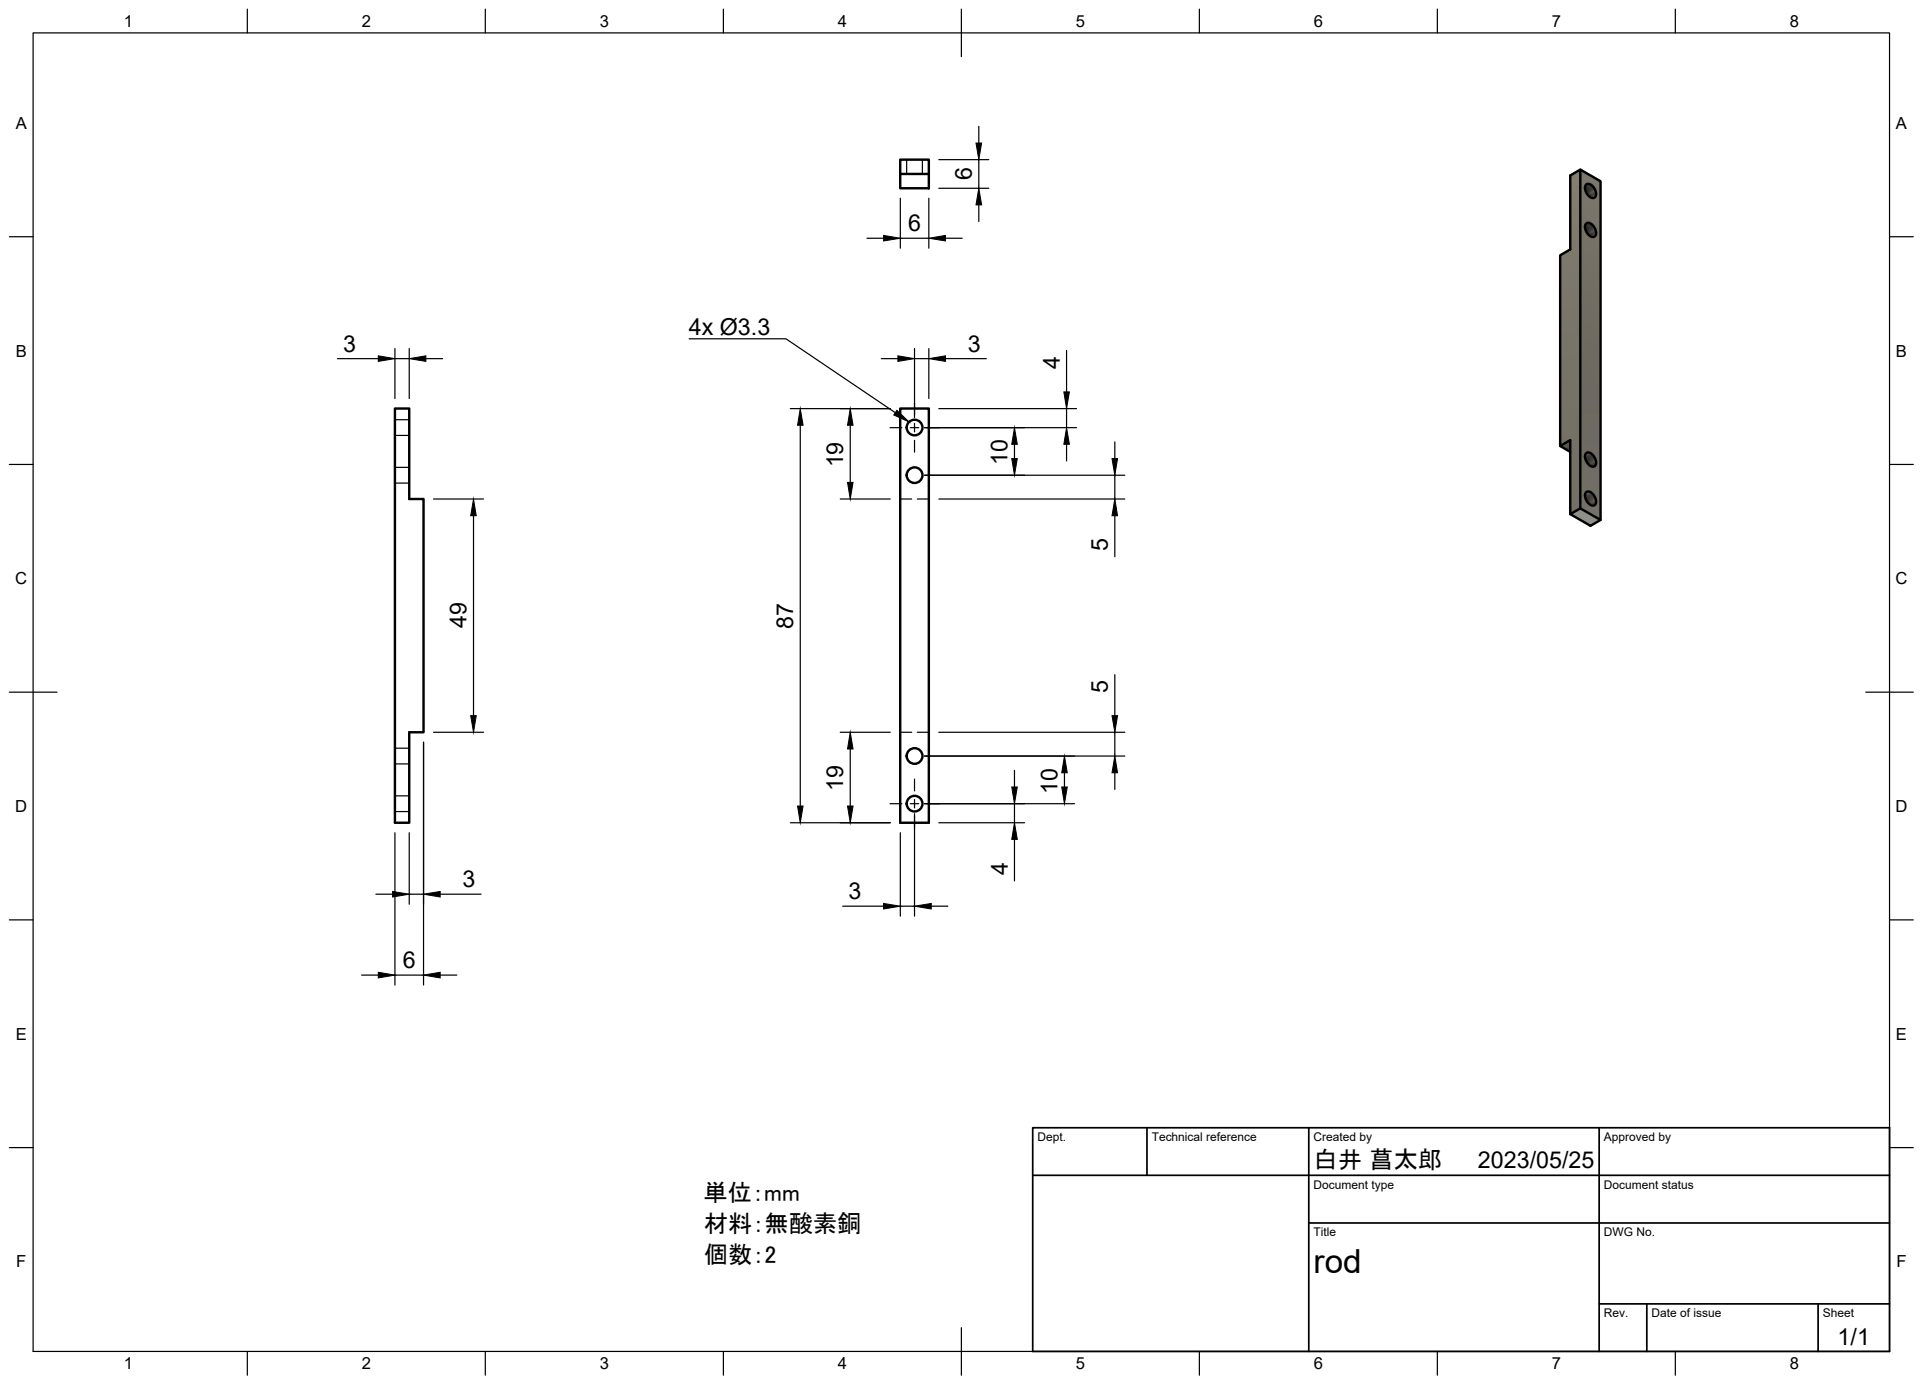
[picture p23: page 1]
Title; DWG No.; Rev.; Date of issue; Sheet; 白井 菖太郎 87

Dept. | Technical reference | Created by 2023/05/25 | Approved by

Document type | Document status
